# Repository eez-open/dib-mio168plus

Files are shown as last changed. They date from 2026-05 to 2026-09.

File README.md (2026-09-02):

### This is a WORK IN PROGRESS!

---

### Ownership and License
The contributors are listed in CONTRIB.TXT. 

Licenses | OSHWA UID
--|--
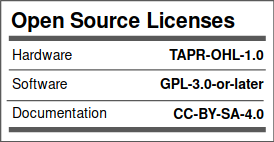
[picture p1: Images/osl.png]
osl
 | OSHW-HR000124 (https://certification.oshwa.org/hr000124.html)

### Overview

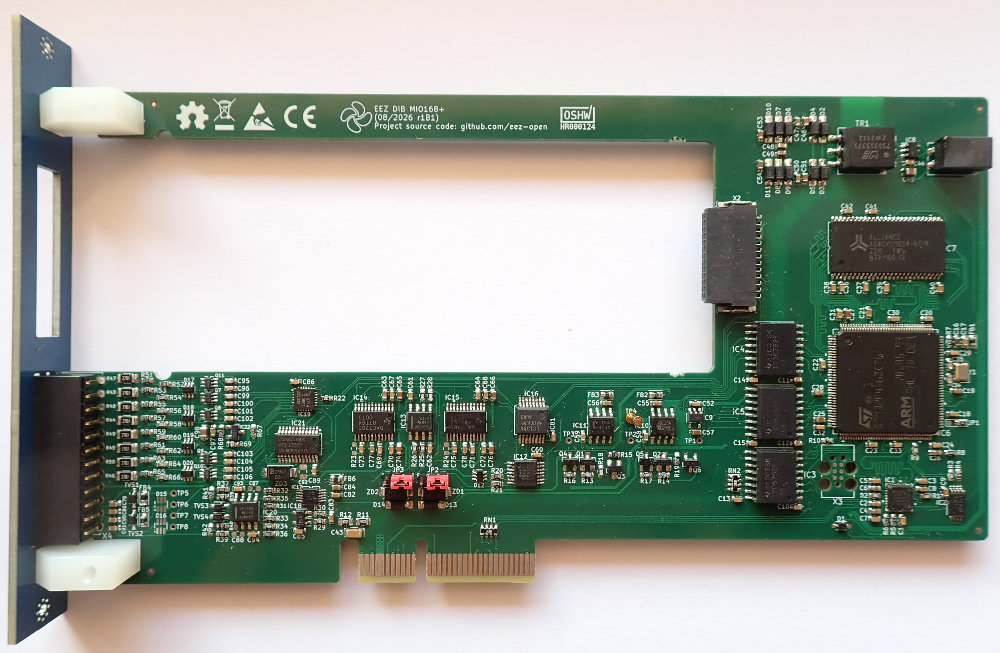
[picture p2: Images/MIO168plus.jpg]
MIO_empty


_Fig 1: MIO168+ without AFE module_

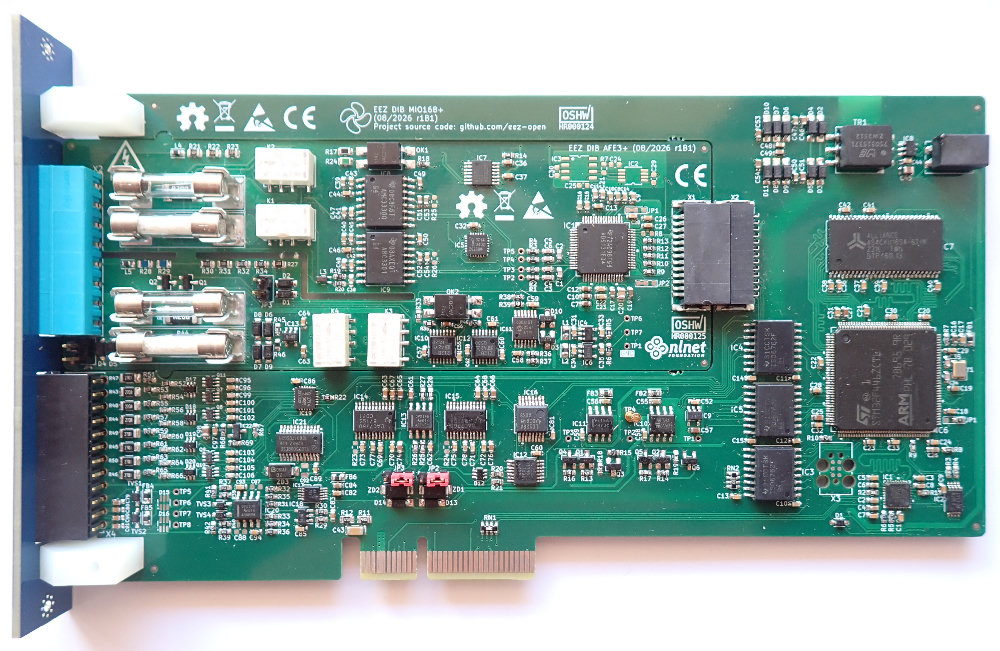
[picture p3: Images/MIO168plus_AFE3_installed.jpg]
MIO_AFE3


_Fig 2: MIO168+ with AFE3+ installed_

The MIO168+ module features multiple digital I/O, analog outputs and expansion connectors for carry various AFEs.

### Feature list

* On-board [STM32F446ZCT6](https://www.st.com/content/st_com/en/products/microcontrollers-microprocessors/stm32-32-bit-arm-cortex-mcus/stm32-high-performance-mcus/stm32f4-series/stm32f446/stm32f446zc.html) high-performance foundation line MCU, ARM Cortex-M4 with DSP and FPU, 256 KiB Flash, LQFP-144 package 
* AFE interface
* 8 x protected digital inputs (3.3/5/24 V), 2 x fast/slow, 6 x slow
* 8 x digital outputs with multiple protections, voltage clamp 24V, nom. current 330 mA (limit 2.3 A)
* 2 x PWM outputs (protected) or sensor bias power (+/-15 V, max. 10 mA)
* 2 x analog bipolar outputs (+/-5 V, +/-10 V, 0-5 V, 0-10 V). Voltage or current output with protection. 12-bit DAC, replaceable with pin compatible 14- or 16-bit version
* 2 x analog bipolar outputs +/-10 V. 12-bit DAC, replaceable with pin compatible 14- or 16-bit version
* On-board isolated power supply with +/-5.3 V outputs (with 4x multipliers), +/-15 V and +3.3 V LDO
* On-board SDRAM for measured data buffering (optional)
* USB HS PHY
* Firmware download via SPI or USB
* Optional SWD for debugging
* I2C EEPROM for storing board specific parameters
* Dimensions: 180 x 95 mm, 4-layer PCB

### Related topics and links

* [EEZ BB3+](https://github.com/eez-open/eez-bb3plus)
* [MIO168+ AFE3](https://github.com/eez-open/dib-mio168plus-afe3)
* [MIO168](https://github.com/eez-open/dib-mio168) for EEZ BB3 (retired)

---

This work is financed by [NLnet](https://nlnet.nl/project/BB3-CM5/) foundation

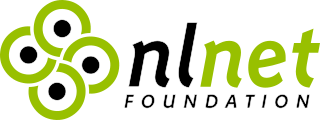
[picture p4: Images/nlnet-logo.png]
nlnet


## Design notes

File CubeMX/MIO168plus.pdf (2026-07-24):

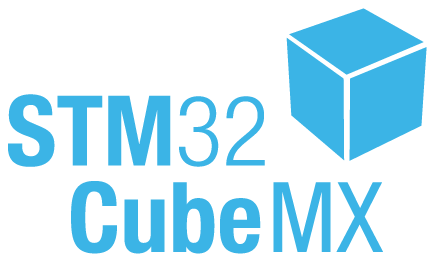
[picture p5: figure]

23/07/2026

MIO168plus Project
Configuration Report

## 1. Description

### 1.1. Project

Project Name | MIO168plus
Board Name | custom
Generated with: | STM32CubeMX 6.17.0
Date | 07/23/2026

### 1.2. MCU

MCU Series | STM32F4
MCU Line | STM32F446
MCU name | STM32F446ZETx
MCU Package | LQFP144
MCU Pin number | 144

### 1.3. Core(s) information

Core(s) | Arm Cortex-M4

## 2. Pinout Configuration

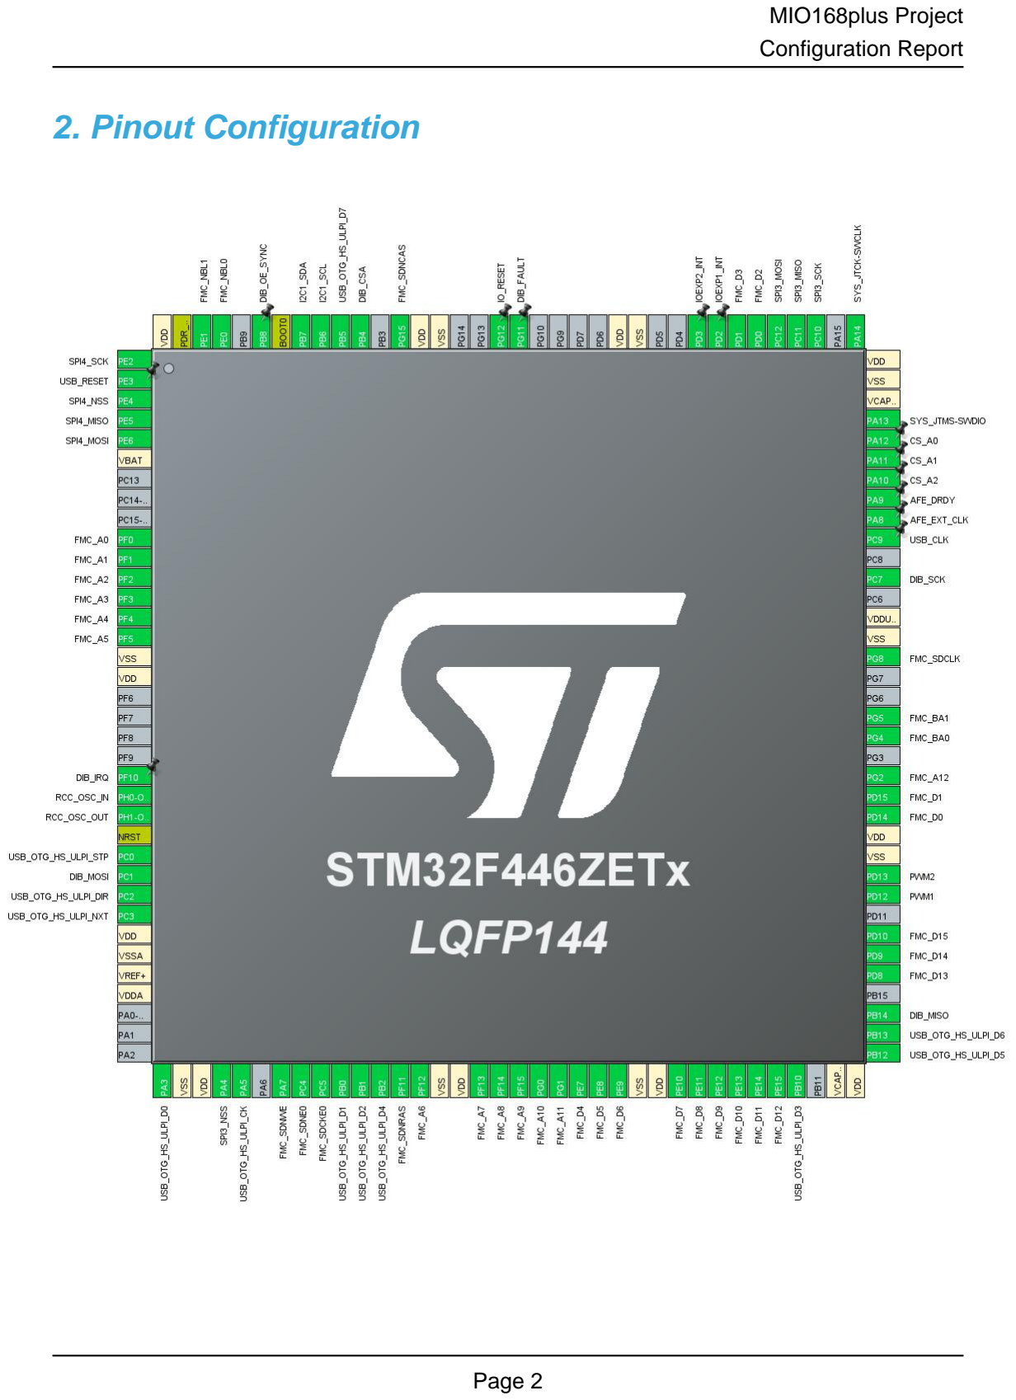
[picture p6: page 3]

## 3. Pins Configuration

Pin Number LQFP144 | Pin Name (function after reset) | Pin Type | Alternate Function(s) | Label
1 | PE2 | I/O | SPI4_SCK
2 | PE3 * | I/O | GPIO_Output | USB_RESET
3 | PE4 | I/O | SPI4_NSS
4 | PE5 | I/O | SPI4_MISO
5 | PE6 | I/O | SPI4_MOSI
6 | VBAT | Power
10 | PF0 | I/O | FMC_A0
11 | PF1 | I/O | FMC_A1
12 | PF2 | I/O | FMC_A2
13 | PF3 | I/O | FMC_A3
14 | PF4 | I/O | FMC_A4
15 | PF5 | I/O | FMC_A5
16 | VSS | Power
17 | VDD | Power
22 | PF10 * | I/O | GPIO_Output | DIB_IRQ
23 | PH0-OSC_IN | I/O | RCC_OSC_IN
24 | PH1-OSC_OUT | I/O | RCC_OSC_OUT
25 | NRST | Reset
26 | PC0 | I/O | USB_OTG_HS_ULPI_STP
27 | PC1 | I/O | SPI2_MOSI | DIB_MOSI
28 | PC2 | I/O | USB_OTG_HS_ULPI_DIR
29 | PC3 | I/O | USB_OTG_HS_ULPI_NXT
30 | VDD | Power
31 | VSSA | Power
32 | VREF+ | Power
33 | VDDA | Power
37 | PA3 | I/O | USB_OTG_HS_ULPI_D0
38 | VSS | Power
39 | VDD | Power
40 | PA4 | I/O | SPI3_NSS
41 | PA5 | I/O | USB_OTG_HS_ULPI_CK
43 | PA7 | I/O | FMC_SDNWE
44 | PC4 | I/O | FMC_SDNE0
45 | PC5 | I/O | FMC_SDCKE0
46 | PB0 | I/O | USB_OTG_HS_ULPI_D1
47 | PB1 | I/O | USB_OTG_HS_ULPI_D2

Pin Number LQFP144 | Pin Name (function after reset) | Pin Type | Alternate Function(s) | Label
48 | PB2 | I/O | USB_OTG_HS_ULPI_D4
49 | PF11 | I/O | FMC_SDNRAS
50 | PF12 | I/O | FMC_A6
51 | VSS | Power
52 | VDD | Power
53 | PF13 | I/O | FMC_A7
54 | PF14 | I/O | FMC_A8
55 | PF15 | I/O | FMC_A9
56 | PG0 | I/O | FMC_A10
57 | PG1 | I/O | FMC_A11
58 | PE7 | I/O | FMC_D4
59 | PE8 | I/O | FMC_D5
60 | PE9 | I/O | FMC_D6
61 | VSS | Power
62 | VDD | Power
63 | PE10 | I/O | FMC_D7
64 | PE11 | I/O | FMC_D8
65 | PE12 | I/O | FMC_D9
66 | PE13 | I/O | FMC_D10
67 | PE14 | I/O | FMC_D11
68 | PE15 | I/O | FMC_D12
69 | PB10 | I/O | USB_OTG_HS_ULPI_D3
71 | VCAP_1 | Power
72 | VDD | Power
73 | PB12 | I/O | USB_OTG_HS_ULPI_D5
74 | PB13 | I/O | USB_OTG_HS_ULPI_D6
75 | PB14 | I/O | SPI2_MISO | DIB_MISO
77 | PD8 | I/O | FMC_D13
78 | PD9 | I/O | FMC_D14
79 | PD10 | I/O | FMC_D15
81 | PD12 | I/O | TIM4_CH1 | PWM1
82 | PD13 | I/O | TIM4_CH2 | PWM2
83 | VSS | Power
84 | VDD | Power
85 | PD14 | I/O | FMC_D0
86 | PD15 | I/O | FMC_D1
87 | PG2 | I/O | FMC_A12
89 | PG4 | I/O | FMC_BA0
90 | PG5 | I/O | FMC_BA1

Pin Number LQFP144 | Pin Name (function after reset) | Pin Type | Alternate Function(s) | Label
93 | PG8 | I/O | FMC_SDCLK
94 | VSS | Power
95 | VDDUSB | Power
97 | PC7 | I/O | SPI2_SCK | DIB_SCK
99 | PC9 | I/O | RCC_MCO_2 | USB_CLK
100 | PA8 | I/O | RCC_MCO_1 | AFE_EXT_CLK
101 | PA9 | I/O | GPIO_EXTI9 | AFE_DRDY
102 | PA10 * | I/O | GPIO_Output | CS_A2
103 | PA11 * | I/O | GPIO_Output | CS_A1
104 | PA12 * | I/O | GPIO_Output | CS_A0
105 | PA13 | I/O | SYS_JTMS-SWDIO
106 | VCAP_2 | Power
107 | VSS | Power
108 | VDD | Power
109 | PA14 | I/O | SYS_JTCK-SWCLK
111 | PC10 | I/O | SPI3_SCK
112 | PC11 | I/O | SPI3_MISO
113 | PC12 | I/O | SPI3_MOSI
114 | PD0 | I/O | FMC_D2
115 | PD1 | I/O | FMC_D3
116 | PD2 | I/O | GPIO_EXTI2 | IOEXP1_INT
117 | PD3 | I/O | GPIO_EXTI3 | IOEXP2_INT
120 | VSS | Power
121 | VDD | Power
126 | PG11 | I/O | GPIO_EXTI11 | DIB_FAULT
127 | PG12 * | I/O | GPIO_Output | IO_RESET
130 | VSS | Power
131 | VDD | Power
132 | PG15 | I/O | FMC_SDNCAS
134 | PB4 | I/O | SPI2_NSS | DIB_CSA
135 | PB5 | I/O | USB_OTG_HS_ULPI_D7
136 | PB6 | I/O | I2C1_SCL
137 | PB7 | I/O | I2C1_SDA
138 | BOOT0 | Boot
139 | PB8 | I/O | GPIO_EXTI8 | DIB_OE_SYNC
141 | PE0 | I/O | FMC_NBL0
142 | PE1 | I/O | FMC_NBL1
143 | PDR_ON | Reset
144 | VDD | Power

* The pin is affected with an I/O function

## 4. Clock Tree Configuration

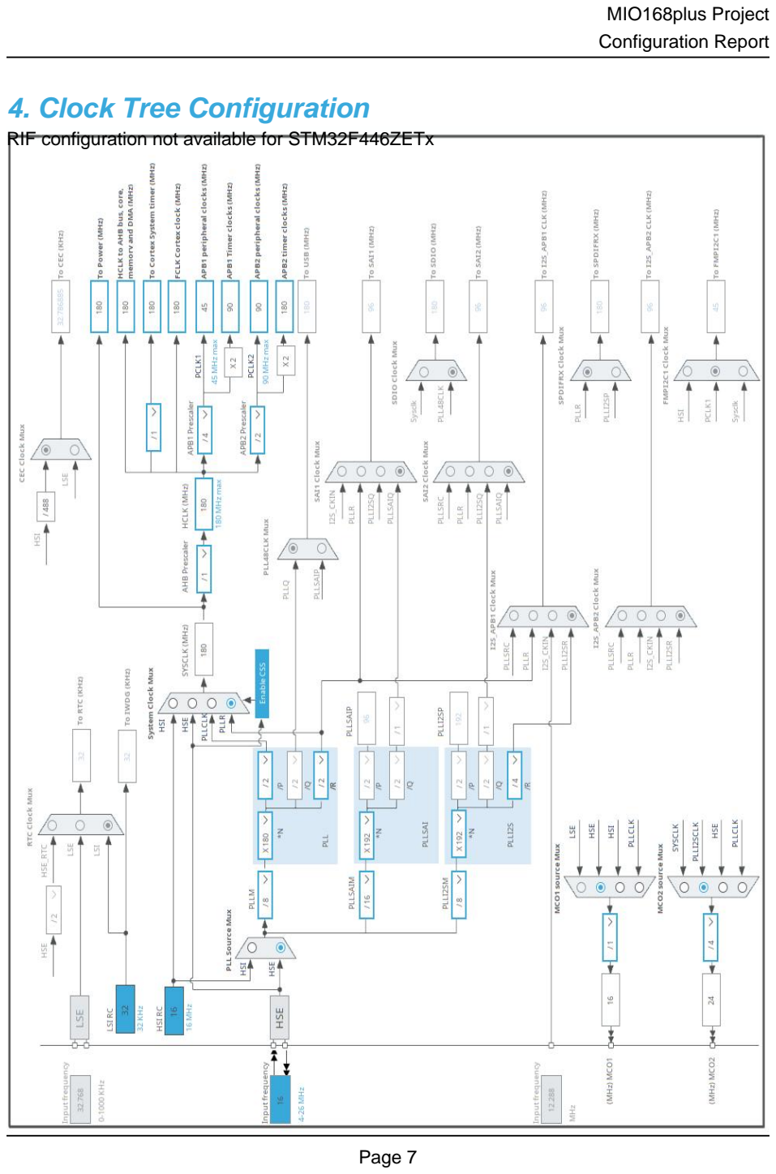
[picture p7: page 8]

RIF configuration not available for STM32F446ZETx

## 1. Power Consumption Calculator report

### 1.1. Microcontroller Selection

Series | STM32F4
Line | STM32F446
MCU | STM32F446ZETx
Datasheet | DS10693_Rev6

### 1.2. Parameter Selection

Temperature | 25
Vdd | 3.3

### 1.3. Battery Selection

Battery | Li-SOCL2(A3400)
Capacity | 3400.0 mAh
Self Discharge | 0.08 %/month
Nominal Voltage | 3.6 V
Max Cont Current | 100.0 mA
Max Pulse Current | 200.0 mA
Cells in series | 1
Cells in parallel | 1

### 1.4. Sequence

Step | Step1 | Step2
Mode | RUN | STOP_UDM (Under Drive)
Vdd | 3.3 | 3.3
Voltage Source | Battery | Battery
Range | Scale1-High | No Scale
Fetch Type | RAM/FLASH/REGON/ART/P REFETCH | n/a
CPU Frequency | 180 MHz | 0 Hz
Clock Configuration | HSE PLL | Regulator_LP Flash-PwrDwn
Clock Source Frequency | 4 MHz | 0 Hz
Peripherals
Additional Cons. | 0 mA | 0 mA
Average Current | 46 mA | 55 µA
Duration | 0.1 ms | 0.9 ms
DMIPS | 225.0 | 0.0
Ta Max | 99.99 | 104.99
Category | In DS Table | In DS Table

### 1.5. Results

Sequence Time | 1 ms | Average Current | 4.65 mA
Battery Life | 1 month | Average DMIPS | 225.0 DMIPS

### 1.6. Chart

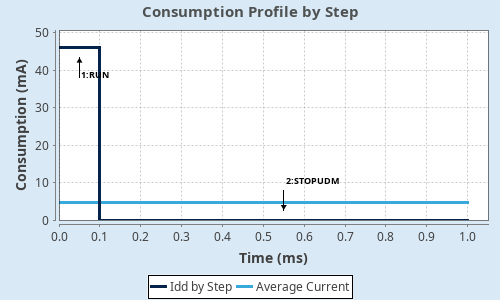
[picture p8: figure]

## 2. Software Project

### 2.1. Project Settings

Name | Value
Project Name | MIO168plus
Project Folder | /home/denis/git-public/dib-mio168plus/CubeMX
Toolchain / IDE | EWARM V8.50
Firmware Package Name and Version | STM32Cube FW_F4 V1.28.3
Application Structure | Advanced
Generate Under Root | No
Do not generate the main() | No
Minimum Heap Size | 0x200
Minimum Stack Size | 0x400

### 2.2. Code Generation Settings

Name | Value
STM32Cube MCU packages and embedded software | Copy all used libraries into the project folder
Generate peripheral initialization as a pair of '.c/.h' files | No
Backup previously generated files when re-generating | No
Keep User Code when re-generating | Yes
Delete previously generated files when not re-generated | Yes
Set all free pins as analog (to optimize the power consumption) | No
Enable Full Assert | No

### 2.3. Advanced Settings - Generated Function Calls

Rank | Function Name | Peripheral Instance Name
1 | SystemClock_Config | RCC
2 | MX_GPIO_Init | GPIO
3 | MX_FMC_Init | FMC
4 | MX_I2C1_Init | I2C1
5 | MX_SPI2_Init | SPI2
6 | MX_SPI3_Init | SPI3
7 | MX_SPI4_Init | SPI4
8 | MX_USB_OTG_HS_PCD_Init | USB_OTG_HS
9 | MX_TIM4_Init | TIM4

## 3. Peripherals and Middlewares Configuration

### 3.1. FMC

SDRAM 1
Clock and chip enable: SDCKE0+SDNE0
Internal bank number: 4 banks Address: 13 bits
Data: 16 bits
Byte enable: set
3.1.1. SDRAM 1:

SDRAM control:

Bank | SDRAM bank 1
Number of column address bits | 8 bits
Number of row address bits | 13 bits
CAS latency | 1 memory clock cycle
Write protection | Disabled
SDRAM common clock | Disabled
SDRAM common burst read | Disabled
SDRAM common read pipe delay | 0 HCLK clock cycle
SDRAM timing in memory clock cycles:
Load mode register to active delay | 16
Exit self-refresh delay | 16
Self-refresh time | 16
SDRAM common row cycle delay | 16
Write recovery time | 16
SDRAM common row precharge delay | 16
Row to column delay | 16

### 3.2. I2C1

I2C: I2C
3.2.1. Parameter Settings:

Master Features:

I2C Speed Mode | Standard Mode
I2C Clock Speed (Hz) | 100000
Slave Features:
Clock No Stretch Mode | Disabled

Primary Address Length selection | 7-bit
Dual Address Acknowledged | Disabled
Primary slave address | 0
General Call address detection | Disabled

### 3.3. RCC

High Speed Clock (HSE): Crystal/Ceramic Resonator mode: Master Clock Output 1
mode: Master Clock Output 2
3.3.1. Parameter Settings:

System Parameters:

VDD voltage (V) | 3.3
Instruction Cache | Enabled
Prefetch Buffer | Enabled
Data Cache | Enabled
Flash Latency(WS) | 5 WS (6 CPU cycle)
RCC Parameters:
HSI Calibration Value | 16
TIM Prescaler Selection | Disabled
HSE Startup Timout Value (ms) | 100
LSE Startup Timout Value (ms) | 5000
Power Parameters:
Power Regulator Voltage Scale | Power Regulator Voltage Scale 1
Power Over Drive | Enabled

### 3.4. SPI2

Mode: Full-Duplex Slave
Hardware NSS Signal: Hardware NSS Input Signal
3.4.1. Parameter Settings:

Basic Parameters:

Frame Format | Motorola
Data Size | 8 Bits
First Bit | MSB First
Clock Parameters:
Clock Polarity (CPOL) | Low

Clock Phase (CPHA) | 1 Edge
Advanced Parameters:
CRC Calculation | Disabled
NSS Signal Type | Input Hardware

### 3.5. SPI3

Mode: Full-Duplex Master
Hardware NSS Signal: Hardware NSS Output Signal
3.5.1. Parameter Settings:

Basic Parameters:

Frame Format | Motorola
Data Size | 8 Bits
First Bit | MSB First
Clock Parameters:
Prescaler (for Baud Rate) | 2
Baud Rate | 22.5 MBits/s *
Clock Polarity (CPOL) | Low
Clock Phase (CPHA) | 1 Edge
Advanced Parameters:
CRC Calculation | Disabled
NSS Signal Type | Output Hardware

### 3.6. SPI4

Mode: Full-Duplex Master
Hardware NSS Signal: Hardware NSS Output Signal
3.6.1. Parameter Settings:

Basic Parameters:

Frame Format | Motorola
Data Size | 8 Bits
First Bit | MSB First
Clock Parameters:
Prescaler (for Baud Rate) | 2
Baud Rate | 45.0 MBits/s *
Clock Polarity (CPOL) | Low
Clock Phase (CPHA) | 1 Edge

Advanced Parameters:

CRC Calculation | Disabled
NSS Signal Type | Output Hardware

### 3.7. SYS

Debug: Serial Wire
Timebase Source: SysTick

### 3.8. TIM4

Channel1: PWM Generation CH1 Channel2: PWM Generation CH2
3.8.1. Parameter Settings:

Counter Settings:

Prescaler (PSC - 16 bits value) | 0
Counter Mode | Up
Counter Period (AutoReload Register - 16 bits value ) | 65535
Internal Clock Division (CKD) | No Division
auto-reload preload | Disable
Trigger Output (TRGO) Parameters:
Master/Slave Mode (MSM bit) | Disable (Trigger input effect not delayed)
Trigger Event Selection | Reset (UG bit from TIMx_EGR)
PWM Generation Channel 1:
Mode | PWM mode 1
Pulse (16 bits value) | 0
Output compare preload | Enable
Fast Mode | Disable
CH Polarity | High
PWM Generation Channel 2:
Mode | PWM mode 1
Pulse (16 bits value) | 0
Output compare preload | Enable
Fast Mode | Disable
CH Polarity | High

### 3.9. USB_OTG_HS

External Phy: Device_Only
3.9.1. Parameter Settings:
Speed | Device High Speed 480MBit/s
Enable internal IP DMA | Disabled
Physical interface | External Phy
Low power | Disabled
Link Power Management | Disabled
Use dedicated end point 1 interrupt | Disabled
VBUS sensing | Disabled
Signal start of frame | Disabled

* User modified value

## 4. System Configuration

### 4.1. GPIO configuration

IP | Pin | Signal | GPIO mode | GPIO pull/up pull down

Max
Speed

User Label

FMC | PF0 | FMC_A0 | Alternate Function Push Pull | No pull-up and no pull-down | Very High
| PF1 | FMC_A1 | Alternate Function Push Pull | No pull-up and no pull-down | Very High
| PF2 | FMC_A2 | Alternate Function Push Pull | No pull-up and no pull-down | Very High
| PF3 | FMC_A3 | Alternate Function Push Pull | No pull-up and no pull-down | Very High
| PF4 | FMC_A4 | Alternate Function Push Pull | No pull-up and no pull-down | Very High
| PF5 | FMC_A5 | Alternate Function Push Pull | No pull-up and no pull-down | Very High
PA7 | FMC_SDNWE Alternate Function Push Pull | No pull-up and no pull-down | Very High
| PC4 | FMC_SDNE0 | Alternate Function Push Pull | No pull-up and no pull-down | Very High
PC5 | FMC_SDCKE0 Alternate Function Push Pull | No pull-up and no pull-down | Very High
PF11 | FMC_SDNRAS Alternate Function Push Pull | No pull-up and no pull-down | Very High
| PF12 | FMC_A6 | Alternate Function Push Pull | No pull-up and no pull-down | Very High
| PF13 | FMC_A7 | Alternate Function Push Pull | No pull-up and no pull-down | Very High
| PF14 | FMC_A8 | Alternate Function Push Pull | No pull-up and no pull-down | Very High
| PF15 | FMC_A9 | Alternate Function Push Pull | No pull-up and no pull-down | Very High
| PG0 | FMC_A10 | Alternate Function Push Pull | No pull-up and no pull-down | Very High
| PG1 | FMC_A11 | Alternate Function Push Pull | No pull-up and no pull-down | Very High
| PE7 | FMC_D4 | Alternate Function Push Pull | No pull-up and no pull-down | Very High
| PE8 | FMC_D5 | Alternate Function Push Pull | No pull-up and no pull-down | Very High
| PE9 | FMC_D6 | Alternate Function Push Pull | No pull-up and no pull-down | Very High
| PE10 | FMC_D7 | Alternate Function Push Pull | No pull-up and no pull-down | Very High
| PE11 | FMC_D8 | Alternate Function Push Pull | No pull-up and no pull-down | Very High
| PE12 | FMC_D9 | Alternate Function Push Pull | No pull-up and no pull-down | Very High
| PE13 | FMC_D10 | Alternate Function Push Pull | No pull-up and no pull-down | Very High
| PE14 | FMC_D11 | Alternate Function Push Pull | No pull-up and no pull-down | Very High
| PE15 | FMC_D12 | Alternate Function Push Pull | No pull-up and no pull-down | Very High
| PD8 | FMC_D13 | Alternate Function Push Pull | No pull-up and no pull-down | Very High
| PD9 | FMC_D14 | Alternate Function Push Pull | No pull-up and no pull-down | Very High
| PD10 | FMC_D15 | Alternate Function Push Pull | No pull-up and no pull-down | Very High
| PD14 | FMC_D0 | Alternate Function Push Pull | No pull-up and no pull-down | Very High
| PD15 | FMC_D1 | Alternate Function Push Pull | No pull-up and no pull-down | Very High
| PG2 | FMC_A12 | Alternate Function Push Pull | No pull-up and no pull-down | Very High
| PG4 | FMC_BA0 | Alternate Function Push Pull | No pull-up and no pull-down | Very High
| PG5 | FMC_BA1 | Alternate Function Push Pull | No pull-up and no pull-down | Very High
| PG8 | FMC_SDCLK | Alternate Function Push Pull | No pull-up and no pull-down | Very High
| PD0 | FMC_D2 | Alternate Function Push Pull | No pull-up and no pull-down | Very High
| PD1 | FMC_D3 | Alternate Function Push Pull | No pull-up and no pull-down | Very High

IP | Pin | Signal | GPIO mode | GPIO pull/up pull down

Max
Speed

User Label

PG15 | FMC_SDNCAS Alternate Function Push Pull | No pull-up and no pull-down | Very High
PE0 | FMC_NBL0 | Alternate Function Push Pull | No pull-up and no pull-down | Very High
PE1 | FMC_NBL1 | Alternate Function Push Pull | No pull-up and no pull-down | Very High
I2C1 | PB6 | I2C1_SCL | Alternate Function Open
Drain

No pull-up and no pull-down Very High
*
PB7 | I2C1_SDA | Alternate Function Open
Drain

No pull-up and no pull-down Very High
*
RCC | PH0-
OSC_IN
RCC_OSC_IN | n/a | n/a | n/a

PH1-
OSC_OUT
RCC_OSC_OUT | n/a | n/a | n/a
PC9 | RCC_MCO_2 | Alternate Function Push Pull | No pull-up and no pull-down | Low | USB_CLK
PA8 | RCC_MCO_1 | Alternate Function Push Pull | No pull-up and no pull-down | Low | AFE_EXT_CLK
SPI2 | PC1 | SPI2_MOSI | Alternate Function Push Pull | No pull-up and no pull-down | Very High
*

DIB_MOSI

PB14 | SPI2_MISO | Alternate Function Push Pull | No pull-up and no pull-down | Very High
*

DIB_MISO

PC7 | SPI2_SCK | Alternate Function Push Pull | No pull-up and no pull-down | Very High
*

DIB_SCK

PB4 | SPI2_NSS | Alternate Function Push Pull | No pull-up and no pull-down | Very High
*

DIB_CSA

SPI3 | PA4 | SPI3_NSS | Alternate Function Push Pull | No pull-up and no pull-down | Very High
*
PC10 | SPI3_SCK | Alternate Function Push Pull | No pull-up and no pull-down | Very High
*
PC11 | SPI3_MISO | Alternate Function Push Pull | No pull-up and no pull-down | Very High
*
PC12 | SPI3_MOSI | Alternate Function Push Pull | No pull-up and no pull-down | Very High
*
SPI4 | PE2 | SPI4_SCK | Alternate Function Push Pull | No pull-up and no pull-down | Very High
*
PE4 | SPI4_NSS | Alternate Function Push Pull | No pull-up and no pull-down | Very High
*
PE5 | SPI4_MISO | Alternate Function Push Pull | No pull-up and no pull-down | Very High
*
PE6 | SPI4_MOSI | Alternate Function Push Pull | No pull-up and no pull-down | Very High
*
SYS | PA13 | SYS_JTMS- | n/a | n/a | n/a

IP | Pin | Signal | GPIO mode | GPIO pull/up pull down

Max
Speed

User Label

SWDIO
| PA14 | SYS_JTCK- SWCLK | n/a | n/a | n/a
TIM4 | PD12 | TIM4_CH1 | Alternate Function Push Pull | No pull-up and no pull-down | Low | PWM1
| PD13 | TIM4_CH2 | Alternate Function Push Pull | No pull-up and no pull-down | Low | PWM2
USB_OTG_ HS | PC0 | USB_OTG_HS_ ULPI_STP | Alternate Function Push Pull | No pull-up and no pull-down | Very High
| PC2 | USB_OTG_HS_ ULPI_DIR | Alternate Function Push Pull | No pull-up and no pull-down | Very High
| PC3 | USB_OTG_HS_ ULPI_NXT | Alternate Function Push Pull | No pull-up and no pull-down | Very High
| PA3 | USB_OTG_HS_ ULPI_D0 | Alternate Function Push Pull | No pull-up and no pull-down | Very High
| PA5 | USB_OTG_HS_ ULPI_CK | Alternate Function Push Pull | No pull-up and no pull-down | Very High
| PB0 | USB_OTG_HS_ ULPI_D1 | Alternate Function Push Pull | No pull-up and no pull-down | Very High
| PB1 | USB_OTG_HS_ ULPI_D2 | Alternate Function Push Pull | No pull-up and no pull-down | Very High
| PB2 | USB_OTG_HS_ ULPI_D4 | Alternate Function Push Pull | No pull-up and no pull-down | Very High
| PB10 | USB_OTG_HS_ ULPI_D3 | Alternate Function Push Pull | No pull-up and no pull-down | Very High
| PB12 | USB_OTG_HS_ ULPI_D5 | Alternate Function Push Pull | No pull-up and no pull-down | Very High
| PB13 | USB_OTG_HS_ ULPI_D6 | Alternate Function Push Pull | No pull-up and no pull-down | Very High
| PB5 | USB_OTG_HS_ ULPI_D7 | Alternate Function Push Pull | No pull-up and no pull-down | Very High
GPIO | PE3 | GPIO_Output | Output Push Pull | No pull-up and no pull-down | Low | USB_RESET
| PF10 | GPIO_Output | Output Push Pull | No pull-up and no pull-down | Low | DIB_IRQ
| PA9 | GPIO_EXTI9 | External Interrupt Mode with Rising edge trigger detection | No pull-up and no pull-down | n/a | AFE_DRDY
| PA10 | GPIO_Output | Output Push Pull | No pull-up and no pull-down | Low | CS_A2
| PA11 | GPIO_Output | Output Push Pull | No pull-up and no pull-down | Low | CS_A1
| PA12 | GPIO_Output | Output Push Pull | No pull-up and no pull-down | Low | CS_A0
| PD2 | GPIO_EXTI2 | External Interrupt Mode with Rising edge trigger detection | No pull-up and no pull-down | n/a | IOEXP1_INT
| PD3 | GPIO_EXTI3 | External Interrupt Mode with Rising edge trigger detection | No pull-up and no pull-down | n/a | IOEXP2_INT
PG11 | GPIO_EXTI11 External Interrupt Mode with
| | | Rising edge trigger detection | No pull-up and no pull-down | n/a | DIB_FAULT
| PG12 | GPIO_Output | Output Push Pull | No pull-up and no pull-down | Low | IO_RESET
| PB8 | GPIO_EXTI8 | External Interrupt Mode with | No pull-up and no pull-down | n/a | DIB_OE_SYNC

IP | Pin | Signal | GPIO mode | GPIO pull/up pull down | Max Speed | User Label
| | | Rising edge trigger detection

### 4.2. DMA configuration

nothing configured in DMA service

### 4.3. NVIC configuration

4.3.1. NVIC
Interrupt Table | Enable | Preenmption Priority | SubPriority
Non maskable interrupt | true | 0 | 0
Hard fault interrupt | true | 0 | 0
Memory management fault | true | 0 | 0
Pre-fetch fault, memory access fault | true | 0 | 0
Undefined instruction or illegal state | true | 0 | 0
System service call via SWI instruction | true | 0 | 0
Debug monitor | true | 0 | 0
Pendable request for system service | true | 0 | 0
System tick timer | true | 15 | 0
PVD interrupt through EXTI line 16 | | unused
Flash global interrupt | | unused
RCC global interrupt | | unused
EXTI line 2 interrupt | | unused
EXTI line 3 interrupt | | unused
EXTI line[9:5] interrupts | | unused
TIM4 global interrupt | | unused
I2C1 event interrupt | | unused
I2C1 error interrupt | | unused
SPI2 global interrupt | | unused
EXTI line[15:10] interrupts | | unused
FMC global interrupt | | unused
SPI3 global interrupt | | unused
USB On The Go HS End Point 1 Out global interrupt | | unused
USB On The Go HS End Point 1 In global interrupt | | unused
USB On The Go HS global interrupt | | unused
FPU global interrupt | | unused
SPI4 global interrupt | | unused
4.3.2. NVIC Code generation

Enabled interrupt Table Select for init
sequence ordering
| | Generate IRQ
| | handler | Call HAL handler
Non maskable interrupt | false | true | false
Hard fault interrupt | false | true | false
Memory management fault | false | true | false
Pre-fetch fault, memory access fault | false | true | false

Enabled interrupt Table | Select for init sequence ordering | Generate IRQ handler | Call HAL handler
Undefined instruction or illegal state | false | true | false
System service call via SWI instruction | false | true | false
Debug monitor | false | true | false
Pendable request for system service | false | true | false
System tick timer | false | true | true

* User modified value

## 5. System Views

5.1. Category view
5.1.1. Current

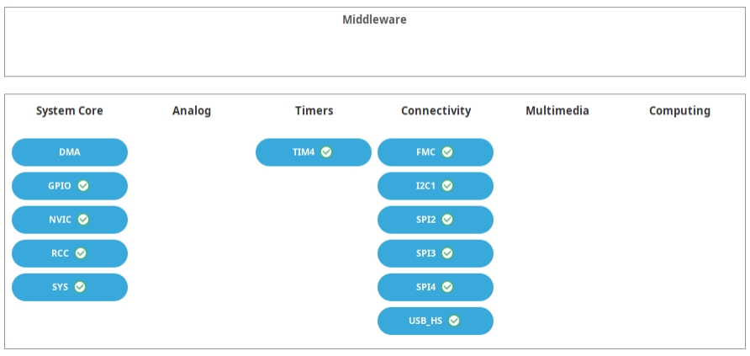
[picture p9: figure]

## 6. Docs & Resources

Type | Link
BSDL files | https://www.st.com/resource/en/bsdl_model/stm32f446_bsdl.zip
IBIS models | https://www.st.com/resource/en/ibis_model/stm32f446_ibis.zip
System View Description | https://www.st.com/resource/en/svd/stm32f4-svd.zip
Presentations | https://www.st.com/resource/en/product_presentation/stm32-stm8_embedded_software_solutions.pdf
Presentations | https://www.st.com/resource/en/product_presentation/stm32_eval-tools_portfolio.pdf
Presentations | https://www.st.com/resource/en/product_presentation/stm32_stm8_functi onal-safety-packages.pdf
Presentations | https://www.st.com/resource/en/product_presentation/stm32-stm8_software_development_tools.pdf
Presentations | https://www.st.com/resource/en/product_presentation/microcontrollers-stm32-family-overview.pdf
Brochures | https://www.st.com/resource/en/brochure/products-and-solutions-for-plcs-and-smart-i-os.pdf
Brochures | https://www.st.com/resource/en/brochure/expansion-boards-for-intelligent-power-switches.pdf
Flyers | https://www.st.com/resource/en/flyer/flstm32nucleo.pdf
Flyers | https://www.st.com/resource/en/flyer/flstm32trust.pdf
Product Certifications | https://www.st.com/resource/en/certification_document/stm32_authentication_can.pdf
Security Bulletin | https://www.st.com/resource/en/technical_note/tn1489-security-bulletin-tn1489stpsirt-physical-attacks-on-stm32-and-stm32cube-firmware-stmicroelectronics.pdf
Application Notes | https://www.st.com/resource/en/application_note/an1709-emc-design-guide-for-stm8-stm32-and-legacy-mcus-stmicroelectronics.pdf
Application Notes | https://www.st.com/resource/en/application_note/an2945-stm8s-and- stm32-mcus-a-consistent-832bit-product-line-for-painless-migration-

| stmicroelectronics.pdf
Application Notes | https://www.st.com/resource/en/application_note/an3070-managing-the-driver-enable-signal-for-rs485-and-iolink-communications-with-the-stm32s-usart-stmicroelectronics.pdf
Application Notes | https://www.st.com/resource/en/application_note/an3126-audio-and-waveform-generation-using-the-dac-in-stm32-products-stmicroelectronics.pdf
Application Notes | https://www.st.com/resource/en/application_note/an3155-usart-protocol-used-in-the-stm32-bootloader-stmicroelectronics.pdf
Application Notes | https://www.st.com/resource/en/application_note/an3156-usb-dfu-protocol-used-in-the-stm32-bootloader-stmicroelectronics.pdf
Application Notes | https://www.st.com/resource/en/application_note/an3364-migration-and-compatibility-guidelines-for-stm32-microcontroller-applications-stmicroelectronics.pdf
Application Notes | https://www.st.com/resource/en/application_note/an3997-audio-playback-and-recording-using-the-stm32f4discovery-stmicroelectronics.pdf
Application Notes | https://www.st.com/resource/en/application_note/an3998-pdm-audio-software-decoding-on-stm32-microcontrollers-stmicroelectronics.pdf
Application Notes | https://www.st.com/resource/en/application_note/an4031-using-the-stm32f2-stm32f4-and-stm32f7-series-dma-controller-stmicroelectronics.pdf
Application Notes | https://www.st.com/resource/en/application_note/an4221-i2c-protocol-used-in-the-stm32-bootloader-stmicroelectronics.pdf
Application Notes | https://www.st.com/resource/en/application_note/an4286-spi-protocol-used-in-the-stm32-bootloader-stmicroelectronics.pdf
Application Notes | https://www.st.com/resource/en/application_note/an4488-getting-started-with-stm32f4xxxx-mcu-hardware-development-stmicroelectronics.pdf
Application Notes | https://www.st.com/resource/en/application_note/an4640-peripherals-interconnections-on-stm32f4057xx-stm32f4157xx-stm32f42xxx-stm32f43xxx-stm32f446xx-and-stm32f469479xx-stmicroelectronics.pdf
Application Notes | https://www.st.com/resource/en/application_note/an4655-virtually-increasing-the-number-of-serial-communication-peripherals-in-stm32-applications-stmicroelectronics.pdf

Application Notes | https://www.st.com/resource/en/application_note/an4658-migration-of-applications-from-stm32f429439-lines-to-stm32f446-line-stmicroelectronics.pdf
Application Notes | https://www.st.com/resource/en/application_note/an4739-stm32cube-firmware-examples-for-stm32f4-series-stmicroelectronics.pdf
Application Notes | https://www.st.com/resource/en/application_note/an4750-handling-of-soft-errors-in-stm32-applications-stmicroelectronics.pdf
Application Notes | https://www.st.com/resource/en/application_note/an4776-generalpurpose-timer-cookbook-for-stm32-microcontrollers-stmicroelectronics.pdf
Application Notes | https://www.st.com/resource/en/application_note/an4803-highspeed-si-simulations-using-ibis-and-boardlevel-simulations-using-hyperlynx-si-on-stm32-mcus-and-mpus-stmicroelectronics.pdf
Application Notes | https://www.st.com/resource/en/application_note/an4850-stm32-mcus-spreadspectrum-clock-generation-principles-properties-and-implementation-stmicroelectronics.pdf
Application Notes | https://www.st.com/resource/en/application_note/an4989-stm32-microcontroller-debug-toolbox-stmicroelectronics.pdf
Application Notes | https://www.st.com/resource/en/application_note/an4995-using-an-electromyogram-technique-to-detect-muscle-activity-stmicroelectronics.pdf
Application Notes | https://www.st.com/resource/en/application_note/an5027-interfacing-pdm-digital-microphones-using-stm32-mcus-and-mpus-stmicroelectronics.pdf
Application Notes | https://www.st.com/resource/en/application_note/an5073-receiving-spdif-audio-stream-with-the-stm32f4f7h7-series-stmicroelectronics.pdf
Application Notes | https://www.st.com/resource/en/application_note/an4760-quadspi-interface-on-stm32-microcontrollers-and-microprocessors--stmicroelectronics.pdf
Application Notes | https://www.st.com/resource/en/application_note/an4899-stm32-microcontroller-gpio-hardware-settings-and-lowpower-consumption-stmicroelectronics.pdf
Application Notes | https://www.st.com/resource/en/application_note/an5612-esd-protection-of-stm32-mcus-and-mpus-stmicroelectronics.pdf
Application Notes | https://www.st.com/resource/en/application_note/an4838-introduction-to-

| memory-protection-unit-management-on-stm32-mcus-stmicroelectronics.pdf
Application Notes | https://www.st.com/resource/en/application_note/an4879-introduction-to-usb-hardware-and-pcb-guidelines-using-stm32-mcus-stmicroelectronics.pdf
Application Notes | https://www.st.com/resource/en/application_note/an5225-introduction-to-usb-typec-power-delivery-for-stm32-mcus-and-mpus-stmicroelectronics.pdf
Application Notes | https://www.st.com/resource/en/application_note/an5537-how-to-use-adc-oversampling-techniques-to-improve-signaltonoise-ratio-on-stm32-mcus-stmicroelectronics.pdf
Application Notes | https://www.st.com/resource/en/application_note/an5036-guidelines-for-thermal-management-on-stm32-applications-stmicroelectronics.pdf
Application Notes | https://www.st.com/resource/en/application_note/an4230-introduction-to-random-number-generation-validation-using-the-nist-statistical-test-suite-for-stm32-mcus-and-mpus-stmicroelectronics.pdf
Application Notes | https://www.st.com/resource/en/application_note/an2867-guidelines-for-oscillator-design-on-stm8afals-and-stm32-mcusmpus-stmicroelectronics.pdf
Application Notes | https://www.st.com/resource/en/application_note/an4013-introduction-to-timers-for-stm32-mcus-stmicroelectronics.pdf
Application Notes | https://www.st.com/resource/en/application_note/an4277-how-to-use-pwm-shutdown-for-motor-control-and-digital-power-conversion-on-stm32-mcus-stmicroelectronics.pdf
Application Notes | https://www.st.com/resource/en/application_note/an4759-introduction-to-using-the-hardware-realtime-clock-rtc-and-the-tamper-management-unit-tamp-with-stm32-mcus-stmicroelectronics.pdf
Application Notes | https://www.st.com/resource/en/application_note/an4908-getting-started-with-usart-automatic-baud-rater-detection-for-stm32-mcus-stmicroelectronics.pdf
Application Notes | https://www.st.com/resource/en/application_note/an5156-introduction-to-security-for-stm32-mcus-stmicroelectronics.pdf
Application Notes | https://www.st.com/resource/en/application_note/an5543-guidelines-for- enhanced-spi-communication-on-stm32-mcus-and-mpus-

| stmicroelectronics.pdf
Application Notes | https://www.st.com/resource/en/application_note/an5992-migrating-from-stm32f446-to-stm32h523533-mcus-stmicroelectronics.pdf
Application Notes | https://www.st.com/resource/en/application_note/cd00211314-how-to-optimize-the-adc-accuracy-in-the-stm32-mcus-stmicroelectronics.pdf
Application Notes | https://www.st.com/resource/en/application_note/an2639-soldering-recommendations-and-package-information-for-leadfree-ecopack2-mcus-and-mpus-stmicroelectronics.pdf
Application Notes | https://www.st.com/resource/en/application_note/an5020-introduction-to-digital-camera-interface-dcmi-for-stm32-mcus-stmicroelectronics.pdf
Application Notes | https://www.st.com/resource/en/application_note/an3154-how-to-use-can-protocol-in-bootloader-on-stm32-mcus-stmicroelectronics.pdf
Application Notes | https://www.st.com/resource/en/application_note/an4566-how-to-extend-the-dac-performance-on-stm32-mcus-stmicroelectronics.pdf
Application Notes | https://www.st.com/resource/en/application_note/an5647-the-goertzel-algorithm-to-compute-individual-terms-of-the-discrete-fourier-transform-dft-in-stm32-products-stmicroelectronics.pdf
Application Notes | https://www.st.com/resource/en/application_note/an2606-introduction-to-system-memory-boot-mode-on-stm32-mcus-stmicroelectronics.pdf
Application Notes for related Tools & Software | https://www.st.com/resource/en/application_note/an2656-stm32f10xxx-lcd-glass-driver-firmware-stmicroelectronics.pdf
Application Notes for related Tools & Software | https://www.st.com/resource/en/application_note/an2790-tft-lcd-interfacing-with-the-highdensity-stm32f10xxx-fsmc-stmicroelectronics.pdf
Application Notes for related Tools & Software | https://www.st.com/resource/en/application_note/an3078-stm32-inapplication-programming-over-the-ic-bus-stmicroelectronics.pdf
Application Notes for related Tools & Software | https://www.st.com/resource/en/application_note/an3116-stm32s-adc-modes-and-their-applications-stmicroelectronics.pdf

Application Notes
for related Tools

https://www.st.com/resource/en/application_note/an3174-implementingreceivers-for-infrared-remote-control-protocols-using-stm32f10xxx-

& Software | microcontrollers-stmicroelectronics.pdf
Application Notes for related Tools & Software | https://www.st.com/resource/en/application_note/an3241-qvga-tftlcd-direct-drive-using-the-stm32f10xx-fsmc-peripheral-stmicroelectronics.pdf
Application Notes for related Tools & Software | https://www.st.com/resource/en/application_note/an3307-guidelines-for-obtaining-iec-60335-class-b-certification-for-any-stm32-application-stmicroelectronics.pdf
Application Notes for related Tools & Software | https://www.st.com/resource/en/application_note/an3965-stm32f40xstm32f41x-inapplication-programming-using-the-usart-stmicroelectronics.pdf
Application Notes for related Tools & Software | https://www.st.com/resource/en/application_note/an3969-eeprom-emulation-in-stm32f40xstm32f41x-microcontrollers-stmicroelectronics.pdf
Application Notes for related Tools & Software | https://www.st.com/resource/en/application_note/an4044-floating-point-unit-demonstration-on-stm32-microcontrollers-stmicroelectronics.pdf
Application Notes for related Tools & Software | https://www.st.com/resource/en/application_note/an4323-getting-started-with-stemwin-library-stmicroelectronics.pdf
Application Notes for related Tools & Software | https://www.st.com/resource/en/application_note/an4365-using-stm32f4-mcu-power-modes-with-best-dynamic-efficiency-stmicroelectronics.pdf
Application Notes for related Tools & Software | https://www.st.com/resource/en/application_note/an4435-guidelines-for-obtaining-ulcsaiec-607301603351-class-b-certification-in-any-stm32-application-stmicroelectronics.pdf
Application Notes for related Tools & Software | https://www.st.com/resource/en/application_note/an4457-implementing-an-emulated-uart-on-stm32f4-microcontrollers-stmicroelectronics.pdf
Application Notes for related Tools & Software | https://www.st.com/resource/en/application_note/an4499-stm32--nrf51822-bluetooth-low-energy-system-solution-stmicroelectronics.pdf
Application Notes for related Tools & Software | https://www.st.com/resource/en/application_note/an4657-stm32-inapplication-programming-iap-using-the-usart-stmicroelectronics.pdf

Application Notes for related Tools & Software | https://www.st.com/resource/en/application_note/an4666-parallel-synchronous-transmission-using-gpio-and-dma-stmicroelectronics.pdf
Application Notes for related Tools & Software | https://www.st.com/resource/en/application_note/an4678-full-duplex-spi-emulation-for-stm32f4-microcontrollers-stmicroelectronics.pdf
Application Notes for related Tools & Software | https://www.st.com/resource/en/application_note/an4701-proprietary-code-readout-protection-on-microcontrollers-of-the-stm32f4-series-stmicroelectronics.pdf
Application Notes for related Tools & Software | https://www.st.com/resource/en/application_note/an4739-stm32cube-firmware-examples-for-stm32f4-series-stmicroelectronics.pdf
Application Notes for related Tools & Software | https://www.st.com/resource/en/application_note/an4758-proprietary-code-readout-protection-on-stm32l4-stm32l4-stm32g4-and-stm32wb-series-mcus-stmicroelectronics.pdf
Application Notes for related Tools & Software | https://www.st.com/resource/en/application_note/an4841-digital-signal-processing-for-stm32-microcontrollers-using-cmsis-stmicroelectronics.pdf
Application Notes for related Tools & Software | https://www.st.com/resource/en/application_note/an4852-programming-an-external-flash-memory-using-the-uart-bootloader-builtin-stm32-microcontrollers-stmicroelectronics.pdf
Application Notes for related Tools & Software | https://www.st.com/resource/en/application_note/an4968-proprietary-code-read-out-protection-pcrop-on-stm32f72xxx-and-stm32f73xxx-microcontrollers-stmicroelectronics.pdf
Application Notes for related Tools & Software | https://www.st.com/resource/en/application_note/an5056-integration-guide-for-the-xcubesbsfu-stm32cube-expansion-package-stmicroelectronics.pdf
Application Notes for related Tools & Software | https://www.st.com/resource/en/application_note/an5360-getting-started-with-projects-based-on-the-stm32mp1-series-in-stm32cubeide-stmicroelectronics.pdf
Application Notes for related Tools & Software | https://www.st.com/resource/en/application_note/an5361-getting-started-with-projects-based-on-dualcore-stm32h7-microcontrollers-in-stm32cubeide-stmicroelectronics.pdf
Application Notes | https://www.st.com/resource/en/application_note/an5394-getting-started-

for related Tools & Software | with-projects-based-on-the-stm32l5-series-in-stm32cubeide-stmicroelectronics.pdf
Application Notes for related Tools & Software | https://www.st.com/resource/en/application_note/an5418-how-to-build-a-simple-usbpd-sink-application-with-stm32cubemx-stmicroelectronics.pdf
Application Notes for related Tools & Software | https://www.st.com/resource/en/application_note/an5426-migrating-graphics-middleware-projects-from-stm32cubemx-540-to-stm32cubemx-550-stmicroelectronics.pdf
Application Notes for related Tools & Software | https://www.st.com/resource/en/application_note/an5464-position-control-of-a-threephase-permanent-magnet-motor-using-xcubemcsdk-or-xcubemcsdkful-stmicroelectronics.pdf
Application Notes for related Tools & Software | https://www.st.com/resource/en/application_note/an5564-getting-started-with-projects-based-on-dualcore-stm32wl-microcontrollers-in-stm32cubeide-stmicroelectronics.pdf
Application Notes for related Tools & Software | https://www.st.com/resource/en/application_note/an5698-adapting-the-xcubestl-functional-safety-package-for-stm32-iec-61508-compliant-to-other-safety-standards-stmicroelectronics.pdf
Application Notes for related Tools & Software | https://www.st.com/resource/en/application_note/an5731-stm32cubemx-and-stm32cubeide-threadsafe-solution-stmicroelectronics.pdf
Application Notes for related Tools & Software | https://www.st.com/resource/en/application_note/an4502-stm32-smbuspmbus-expansion-package-for-stm32cube-stmicroelectronics.pdf
Application Notes for related Tools & Software | https://www.st.com/resource/en/application_note/an5952-how-to-use-cmake-in-stm32cubeide-stmicroelectronics.pdf
Application Notes for related Tools & Software | https://www.st.com/resource/en/application_note/an5054-how-to-perform-secure-programming-using-stm32cubeprogrammer-stmicroelectronics.pdf
Application Notes for related Tools & Software | https://www.st.com/resource/en/application_note/an6179-how-to-integrate-the-stl-firmware-into-a-time-critical-user-application-stmicroelectronics.pdf

Application Notes
for related Tools

https://www.st.com/resource/en/application_note/an6127-getting-startedwith-stm32h7rx7sx-mcus-in-stm32cubeide-stmicroelectronics.pdf

& Software
Application Notes for related Tools & Software | https://www.st.com/resource/en/application_note/an6265-getting-started-with-stm32n6-mcus-in-stm32cubeide-stmicroelectronics.pdf
Application Notes for related Tools & Software | https://www.st.com/resource/en/application_note/an6382-introduction-to-swd-multidrop-for-stm32-with-stlink-stmicroelectronics.pdf
Errata Sheets | https://www.st.com/resource/en/errata_sheet/es0298-stm32f446xcxe-device-errata-stmicroelectronics.pdf
Datasheet | https://www.st.com/resource/en/datasheet/dm00141306.pdf
Programming Manuals | https://www.st.com/resource/en/programming_manual/pm0214-stm32-cortexm4-mcus-and-mpus-programming-manual-stmicroelectronics.pdf
Reference Manuals | https://www.st.com/resource/en/reference_manual/rm0390-stm32f446xx-advanced-armbased-32bit-mcus-stmicroelectronics.pdf
Technical Notes & Articles | https://www.st.com/resource/en/technical_note/tn0516-overview-of-the-stm32f0xf100xxf103xx-and-stm32f2xxf30xf4xx-mcus-pmsm-singledual-foc-sdk-v40-stmicroelectronics.pdf
Technical Notes & Articles | https://www.st.com/resource/en/technical_note/tn1163-description-of-wlcsp-for-microcontrollers-and-recommendations-for-its-use-stmicroelectronics.pdf
Technical Notes & Articles | https://www.st.com/resource/en/technical_note/tn1204-tape-and-reel-shipping-media-for-stm32-microcontrollers-in-bga-packages-stmicroelectronics.pdf
Technical Notes & Articles | https://www.st.com/resource/en/technical_note/tn1205-tape-and-reel-shipping-media-for-stm8-and-stm32-microcontrollers-in-fpn-packages-stmicroelectronics.pdf
Technical Notes & Articles | https://www.st.com/resource/en/technical_note/tn1206-tape-and-reel-shipping-media-for-stm8-and-stm32-microcontrollers-in-qfp-packages-stmicroelectronics.pdf
Technical Notes & Articles | https://www.st.com/resource/en/technical_note/tn1207-tape-and-reel-shipping-media-for-stm8-and-stm32-microcontrollers-in-so-packages-stmicroelectronics.pdf
Technical Notes | https://www.st.com/resource/en/technical_note/tn1208-tape-and-reel-

& Articles | shipping-media-for-stm8-and-stm32-microcontrollers-in-tssop-and-ssop-packages-stmicroelectronics.pdf
Technical Notes & Articles | https://www.st.com/resource/en/technical_note/tn1433-reference-device-marking-schematics-for-stm32-microcontrollers-and-microprocessors-stmicroelectronics.pdf
User Manuals | https://www.st.com/resource/en/user_manual/um3461-stm32f4-series-ulcsaiec-607301603351-selftest-library-user-guide-stmicroelectronics.pdf

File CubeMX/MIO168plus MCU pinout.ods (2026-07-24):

Pin Nb | PINs | FUNCTIONs | LABELs
1 | PE2 | SPI4_SCK
2 | PE3 | GPIO_Output | USB_RESET
3 | PE4 | SPI4_NSS
4 | PE5 | SPI4_MISO
5 | PE6 | SPI4_MOSI
10 | PF0 | FMC_A0
11 | PF1 | FMC_A1
12 | PF2 | FMC_A2
13 | PF3 | FMC_A3
14 | PF4 | FMC_A4
15 | PF5 | FMC_A5
22 | PF10 | GPIO_Output | DIB_IRQ
23 | PH0-OSC_IN | RCC_OSC_IN
24 | PH1-OSC_OUT | RCC_OSC_OUT
26 | PC0 | USB_OTG_HS_ULPI_STP
27 | PC1 | SPI2_MOSI | DIB_MOSI
28 | PC2 | USB_OTG_HS_ULPI_DIR
29 | PC3 | USB_OTG_HS_ULPI_NXT
37 | PA3 | USB_OTG_HS_ULPI_D0
40 | PA4 | SPI3_NSS
41 | PA5 | USB_OTG_HS_ULPI_CK
43 | PA7 | FMC_SDNWE
44 | PC4 | FMC_SDNE0
45 | PC5 | FMC_SDCKE0
46 | PB0 | USB_OTG_HS_ULPI_D1
47 | PB1 | USB_OTG_HS_ULPI_D2
48 | PB2 | USB_OTG_HS_ULPI_D4
49 | PF11 | FMC_SDNRAS
50 | PF12 | FMC_A6
53 | PF13 | FMC_A7
54 | PF14 | FMC_A8
55 | PF15 | FMC_A9
56 | PG0 | FMC_A10
57 | PG1 | FMC_A11
58 | PE7 | FMC_D4
59 | PE8 | FMC_D5
60 | PE9 | FMC_D6
63 | PE10 | FMC_D7
64 | PE11 | FMC_D8
65 | PE12 | FMC_D9
66 | PE13 | FMC_D10
67 | PE14 | FMC_D11
68 | PE15 | FMC_D12
69 | PB10 | USB_OTG_HS_ULPI_D3
73 | PB12 | USB_OTG_HS_ULPI_D5
74 | PB13 | USB_OTG_HS_ULPI_D6
75 | PB14 | SPI2_MISO | DIB_MISO
77 | PD8 | FMC_D13
78 | PD9 | FMC_D14
79 | PD10 | FMC_D15
81 | PD12 | TIM4_CH1 | PWM1
82 | PD13 | TIM4_CH2 | PWM2
85 | PD14 | FMC_D0
86 | PD15 | FMC_D1
87 | PG2 | FMC_A12
89 | PG4 | FMC_BA0
90 | PG5 | FMC_BA1
93 | PG8 | FMC_SDCLK
97 | PC7 | SPI2_SCK | DIB_SCK
99 | PC9 | RCC_MCO_2 | USB_CLK
100 | PA8 | RCC_MCO_1 | AFE_EXT_CLK
101 | PA9 | GPIO_EXTI9 | AFE_DRDY
102 | PA10 | GPIO_Output | CS_A2
103 | PA11 | GPIO_Output | CS_A1
104 | PA12 | GPIO_Output | CS_A0
105 | PA13 | SYS_JTMS-SWDIO
109 | PA14 | SYS_JTCK-SWCLK
111 | PC10 | SPI3_SCK
112 | PC11 | SPI3_MISO
113 | PC12 | SPI3_MOSI
114 | PD0 | FMC_D2
115 | PD1 | FMC_D3
116 | PD2 | GPIO_EXTI2 | IOEXP1_INT
117 | PD3 | GPIO_EXTI3 | IOEXP2_INT
126 | PG11 | GPIO_EXTI11 | DIB_FAULT
127 | PG12 | GPIO_Output | IO_RESET
132 | PG15 | FMC_SDNCAS
134 | PB4 | SPI2_NSS | DIB_CSA
135 | PB5 | USB_OTG_HS_ULPI_D7
136 | PB6 | I2C1_SCL
137 | PB7 | I2C1_SDA
139 | PB8 | GPIO_EXTI8 | DIB_OE_SYNC
141 | PE0 | FMC_NBL0
142 | PE1 | FMC_NBL1

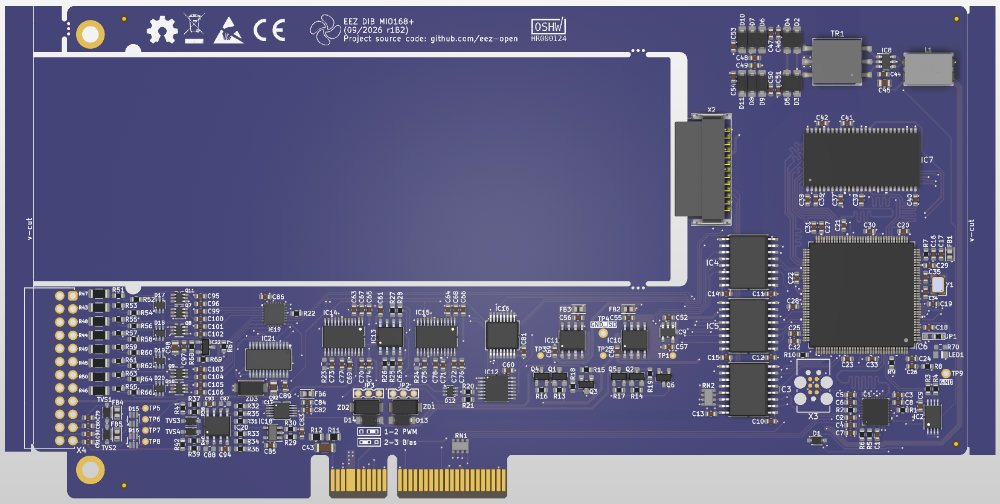
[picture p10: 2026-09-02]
Images/MIO168plus_3D.jpg

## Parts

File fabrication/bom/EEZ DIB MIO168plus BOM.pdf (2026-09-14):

EEZ DIB MIO168plus BOM, 14.09.2026

# | Reference | Value | Qty | DigiKey | Mouser | TME | LCSC

1 | | 100n | 57 | 490-4774-1-ND | 80-C0603C104M4R | CL10B104KA8NNNC | C14663
2 | 4u7/35V | 13 | 1276-6794-1-ND | GRM219R6YA475KA73D C913498
3 | C16,C47,C48,C49,C50,C55,C56 | 1u/50V | 7 | 1276-1860-1-ND | 187-CL10A105KB8NNNC CL10A105KB8NNNC | C15849
4 | C25,C27,C57 | 2u2 | 3 | 490-12738-1-ND | GRM188R61E225KA12D C77047
5 | C34,C35 | 10p | 2 | 1276-1069-1-ND | 187-CL10C100CB8NNNC VJ0603A100JXACW1BC C1634
6 | C43 | 4n7/1kV | 1 | 732-12074-2-ND | 710-885342208020 | 1206B472K102CT | C303960
7 | C45,C92,C98 | 10u | 3 | 490-5523-1-ND | GRM21BR61E106KA73L C15850
8 | C69,C71 | 2n2 | 2 | 490-4931-1-ND | GCM188R71H222KA37D C161225
9 | C77,C78 | 22n | 2 | 490-4933-1-ND | GCM188R71H223KA37D C161226
10 | C79,C80,C90,C91 | 1n | 4 | 1276-1018-2-ND | 187-CL10B102KB8NNNC CL10B102KB8NNNC | C1588
11 | C95,C99,C106 | 100p | 3 | 490-11153-1-ND | 81-GCM1885C1H101JA6J GCM1885C1H101JA16J C3868042
12 | C96,C100,C101,C102,C103,C104,C105 10n | 7 | 1276-1009-1-ND | 187-CL10B103KB8NNNC CL10B103KB8NNNC | C57112
13 | D1 | BAS316 | 1 | 1727-7370-1-ND | 771-BAS316-T/R | BAS316,115 | C109218
14 | MBR0530T3G | 12 | 863-MBR0530T3G | MBR0530T3GOSCT-ND MBR0530T3G | C236079
15 | D12,D17,D18,D19,D20 | BAT54XYH | 5 | 1727-2723-1-ND | 771-BAT54XYH | BAT54XY.115 | C549283
16 | FB1,FB2,FB3,FB4,FB5,FB6 | BLM18AG102SH1D | 6 | 490-7809-1-ND | 81-BLM18AG102SH1D | BLM18AG102SH1D | C337877
17 | IC1 | USB3300-EZK | 1 | 638-1034-ND | 886-USB3300-EZK | - | C108383
18 | IC2 | M24C32-DFDW6TP | 1 | 497-16067-1-ND | 511-M24C32-DFDW6TP M24C32-DFDW6TP | C2971426
19 | IC3,IC4,IC5 | ISO6762FDWR | 3 | 296-ISO6762FDWRCT-ND | 595-ISO6762FDWR | - | C5216396
20 | IC6 | STM32F446ZET6 | 1 | 497-15374-ND | 511-STM32F446ZET6 | STM32F446ZET6 | C1337227
21 | IC7 | IS42S16400N-6TL | 1 | 1450-1260-ND | 822-IM6416SDBATG-6I | - | C62379
22 | IC8 | SN6505BDBVT | 1 | 296-43154-2-ND | 595-SN6505BDBVT | - | C2156022
23 | IC9 | TPS7A2033PDBVR | 1 | 296-TPS7A2033PDBVRCT-ND | 595-TPS7A2033PDBVR | TPS7A2033PDBVR | C2862740
24 | IC10 | MC78L15ACDR2G | 1 | MC78L15ACDR2GOSDKR-ND | 863-MC78L15ACDR2G | L78L15ACD13TR | C233225
25 | IC11 | MC79L15ACDR2G | 1 | MC79L15ABDR2GOSDKR | 863-MC79L15ACDR2G | MC79L15ACDG | C148319
26 | IC12 | 74HC126PW,118 | 1 | 1727-6579-1-ND | 771-HC126PW118 | SN74HC126PWR | C507234
27 | IC13,IC20 | OPA2196IDR | 2 | 296-48159-1-ND | 595-OPA2196IDR | OPA2196IDR | C2057972
28 | IC14,IC15 | DAC7760IPWPR | 2 | 296-37188-1-ND | 595-DAC7760IPWPR | - | C2651670
29 | IC16 | SN74LVC138ADBR | 1 | 296-8460-1-ND | 595-SN74LVC138ADBR - | C2674435
30 | IC17 | DAC7563TDGSR | 1 | 296-43287-1-ND | 595-DAC7563TDGSR | - | C2879196
31 | IC18 | OPA376AIDBVR | 1 | 296-39130-2-ND | 595-OPA376AIDBVR | OPA376AIDBVR | C42134
32 | IC19 | PCAL9714HNMP | 1 | 568-PCAL9714HNMPCT-ND | 771-PCAL9714HNMP | - | C22444745
33 | IC21 | TLE75008ESDXUMA1 | 1 | 448-TLE75008ESDXUMA1CT-ND | | - | C2150432

C1,C2,C3,C5,C7,C9,C10,C11,C12,C13, C14,C15,C17,C18,C19,C20,C21,C22,C2 3,C24,C28,C29,C30,C31,C32,C33,C36, C37,C38,C39,C40,C41,C42,C44,C52,C5 8,C59,C60,C61,C62,C63,C64,C67,C68, C70,C72,C73,C75,C81,C82,C83,C85,C8 6,C89,C93,C94,C97
C4,C6,C8,C26,C46,C51,C53,C54,C65,C 66,C74,C76,C84

81-
GRM188R6YA475ME5D

81-
GRM188R61E225KA2D

81-
GRM21BR61E106KA3L
81-
GCM188R71H222K37D
81-
GCM188R71H223KA7J

D2,D3,D4,D5,D6,D7,D8,D9,D10,D11,D1 3,D14

726-
TLE75008ESDXUMA1

EEZ DIB MIO168plus BOM, 14.09.2026

34 | IC22 | TL431B | 1 | 296-17332-1-ND | 595-TL431IDBZR | L431QDBZR.215 | C21235
35 | JP2,JP3 | DS1025-01-1*3P8BV1-B | 2 | 952-1312-ND | 855-M22-2510305 | ZL303-03P | C3324237
36 | KK1,KK2 | PCB-MB-01 | 2 | RPC1760-ND | 144-PCB-MB-01 | RI-PCB-MB-01 | C959626
37 | L1 | SRF0905-202Y | 1 | SRF0905-202YCT-ND | 652-SRF0905-202Y | - | C2651160
38 | Q1 | MMBT5401 | 1 | MMBT5401-FDICT-ND | 621-MMBT5401-F | MMBT5401 | C21488
39 | Q2,Q3 | MMBT5551 | 2 | MMBT5551LT1GOSCT-ND | 863-MMBT5551LT1G | MMBT5551 | C83942
40 | Q4,Q6 | DMP3099L | 2 | DMP3099L-13DICT-ND | 621-DMP3099L-7 | DMP3099L-7 | C155244
41 | Q5 | 2N7002 | 1 | 2N7002LT1GOSCT-ND | 863-2N7002LT1G | 2N7002LT1G | C16338
42 | Q7,Q8,Q9,Q10,Q11 | NTJD5121NT1G | 5 | NTJD5121NT1GOSCT-ND | 863-NTJD5121NT1G | NTJD5121NT1G | C15215
43 | R1,R2,R25,R26,R27,R28 | 15R | 6 | 13-AC0603FR-0715RLCT-ND | 603-AC0603FR-0715RL | CQ0603-15R-1% | C144698
44 | R3,R4,R69 | 1K8 | 3 | 13-RC0603FR-131K8LCT-ND | 603-RC0603FR-131K8L | SMD0603-1K8-1% | C4177
45 | R5,R15,R68 | 470R | 3 | 13-AC0603FR-7W470RLCT-ND | 603-AC0603FR-7W470RL SMD0603-470R-1% | C20142029
46 | R6 | 12K | 1 | 13-RC0603FR-1312KLCT-ND | 603-RC0603FR-0712KL | SMD0603-12K-1% | C114659
47 | R7,R13,R14,R41,R42 | 47R | 5 | 13-RC0603FR-1347RLCT-ND | 603-RC0603FR-1347RL | SMD0603-47R-1% | C4328334
48 | R8 | 1R | 1 | 652-CR0603-F/1R00ELF SMD0603-1R-1% | C163871
49 | R9,R18,R19,R22 | 10K | 4 | 1712-CRGH0603F10KCT-ND | 756-WCR0603-10KFI | SMD0603-10K-1% | C25804
50 | R10 | 4K7 | 1 | 13-RC0603FR-134K7LTR-ND | 603-RC0603FR-134K7L | SMD0603-4K7-1% | C23162
51 | R11,R12 | 470K | 2 | A126370CT-ND | 71-CRCW0805470KFKEA 0805S8J0474T5E | C17709
52 | R16,R17 | 100K | 2 | 311-100KHRCT-ND | 603-RC0603FR-07100KL SMD0603-100K-1% | C25803
53 | R20,R21,R67 | 100R | 3 | 13-RC0603FR-10100RLCT-ND | 603-RC0603FR-10100RL RC0603FR-10100RL | C22775
54 | R29,R30,R31,R32,R33,R34 | 9K09 0.1% | 6 | YAG4788CT-ND | 603-RC0603BR-079K09L AR0603-9K09-0.1% | C185301
55 | R35,R36,R37,R39 | 75K 0.1% | 4 | YAG1730CT-ND | 603-RT0603BRD0775KL AR0603-75K-0.1% | C723587
56 | R38,R40 | 180R | 2 | 13-RC0603FR-13180RLCT-ND | 603-RC0603FR-13180RL SMD0603-180R-1% | C4077604
57 | R43,R44,R45,R46,R47,R48,R49,R50 | 2K7 | 8 | 311-2.70KFRCT-ND | 652-CR1206FX-2701ELF 1206S4F2701T5E | C205261
58 | R51,R53,R55,R57,R59,R61,R63,R65 | 27K | 8 | 311-27.0KHRCT-ND | 603-RC0603FR-0727KL | SMD0603-27K-1% | C114614
59 | R52,R54,R56,R58,R60,R62,R64,R66 | 1K | 8 | 13-RC0603FR-131KLCT-ND | 603-RC0603FR-131KL | CQ0603-1K-1% | C21190
60 | RN1,RN2 | CAY16-330J4LF | 2 | CAY16-330J4LFCT-ND | 652-CAY16-330J4LF | 4D03WGJ0330T | C840641
61 | TR1 | 750315371 | 1 | 1297-1178-1-ND | 710-750315371 | - | -
62 | TVS1,TVS2,TVS3,TVS4 | SD12C-7 | 4 | 31-SD12C-7CT-ND | 621-SD12C-7 | SD12C-7 | C1977377
63 | X2 | | 1 | | - | - | C5611301
64 | X4 | 1844824 | 1 | 1844824-ND | 651-1844824 | - | C6790362
65 | Y1 | | 1 | 535-14383-1-ND | | CX3225FB16000F0FZZ | C1986769
66 | ZD1,ZD2 | SMF16A | 2 | 4878-SMF16ATR-ND | 637-SMF16A | SMF16A-DIO | C207257
67 | ZD3 | SMF24A | 1 | 4878-SMF24ACT-ND | 637-SMF24A | SMF24A-DIO | C315999

118-CHP0603QFW-1R00ELFCT-ND

CBED202-
1379B001C1AD

4217-CBED202-
1379B001C1ADCT-ND

ABM8-16.000MHZ-10-
D7G-T

815-
ABM816.MHZ10D7GT

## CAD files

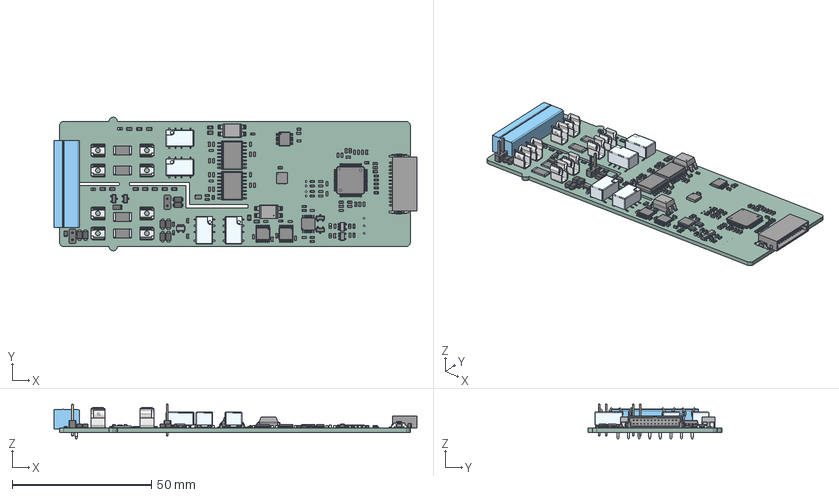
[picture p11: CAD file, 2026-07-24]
KiCad/MIO168plus AFE3.step
130.4 x 48.0 x 12.5 mm
C_0603_1608Metric x 60
R_0805_2012Metric x 15
R_0603_1608Metric x 23
ERJU1T0R00U x 4
IM03DGR x 4
BODY-SOIC x 2
LEAD-DW0016 x 32
PinsArrayL
PinsArrayR
PinHeader_1x02_P254mm_Vertical x 2
DG409LEDQ-T1-GE3 x 2
Body001 (Mirror #1) x 7
XY-plane x 12
X-axis x 12
GBED204-13-HSG
GBED204-Terminal2 x 13
GBED204-Terminal x 13
GBED204-Ground Piece x 2
R_1206_3216Metric
ThermalPin
PinsArrayLR
PinsArrayTB
MCP41HV51-103E_ST
BODY_VEC64A
LEAD_VEC64A x 64
CUI_DEVICES_TBP02R1-381-08BE
EEZ DIB AFE3plus_PCB

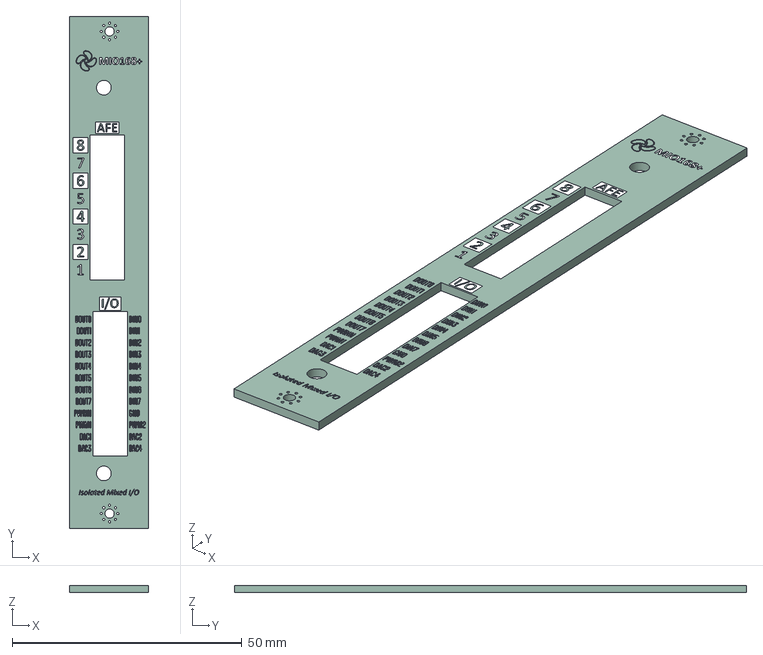
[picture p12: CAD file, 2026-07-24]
fabrication/step/MIO168plus front mask.step
17.2 x 111.5 x 1.58 mm
EEZ DIB MIO168plus front mask.kicad_pro_silkscreen
EEZ DIB MIO168plus front mask.kicad_pro_PCB

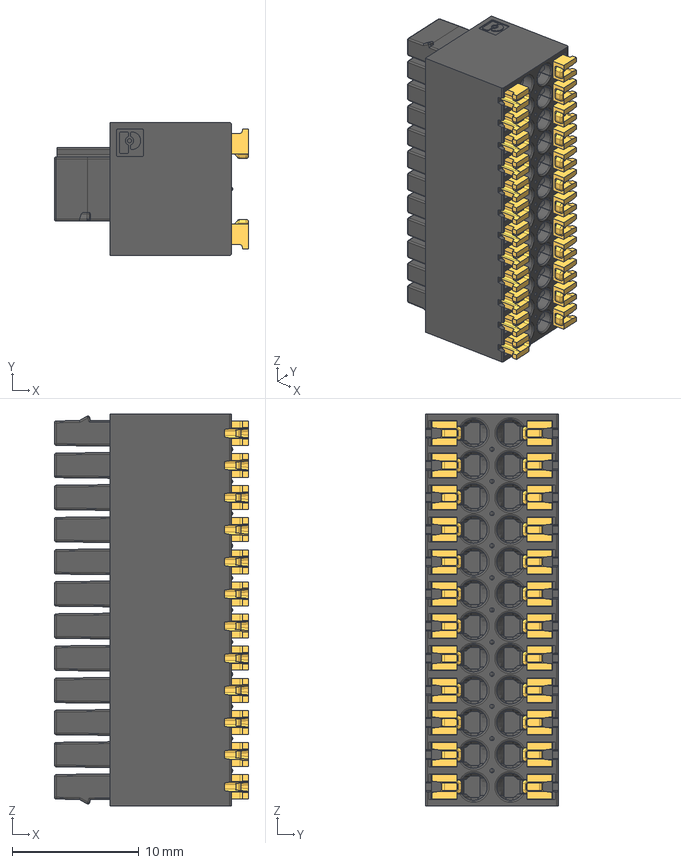
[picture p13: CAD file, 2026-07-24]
fabrication/step/1844675.stp
15.4 x 10.5 x 31.0 mm

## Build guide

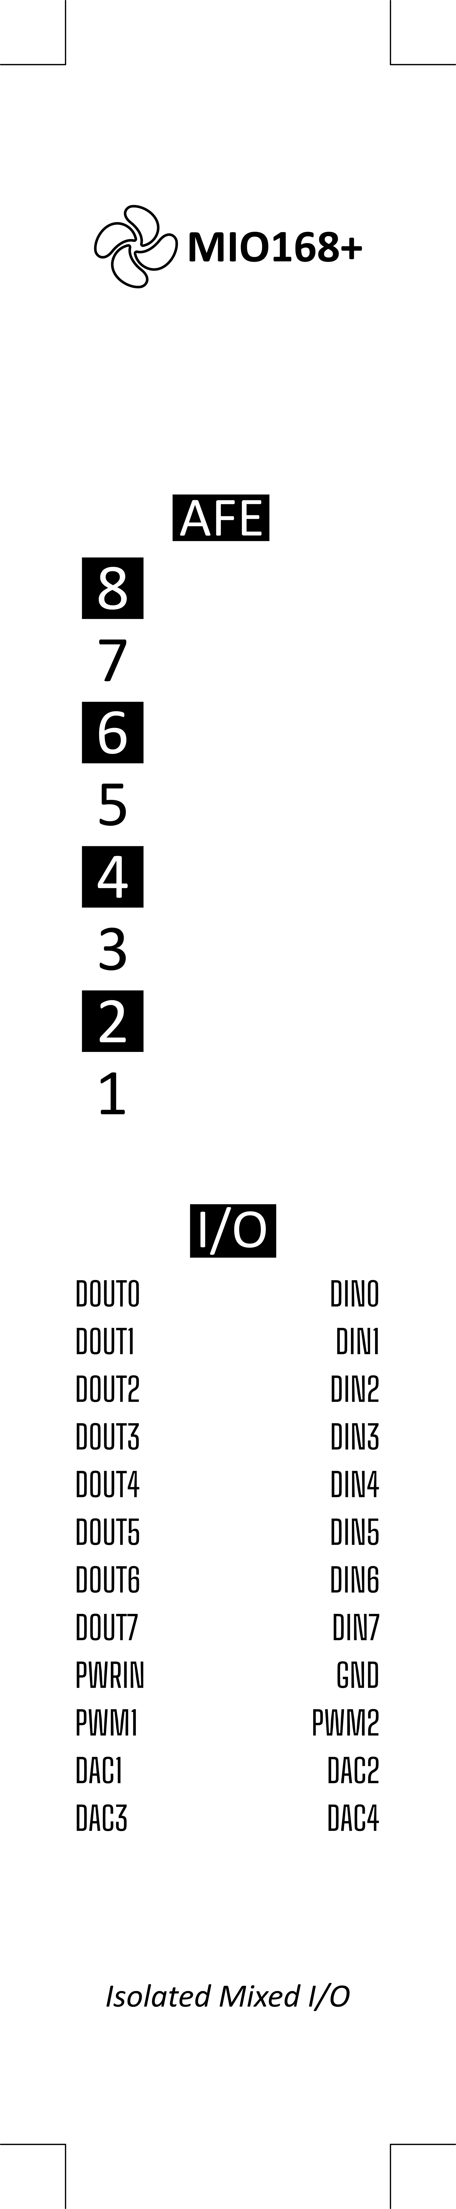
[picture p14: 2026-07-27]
fabrication/front mask/MIO168plus front mask.png

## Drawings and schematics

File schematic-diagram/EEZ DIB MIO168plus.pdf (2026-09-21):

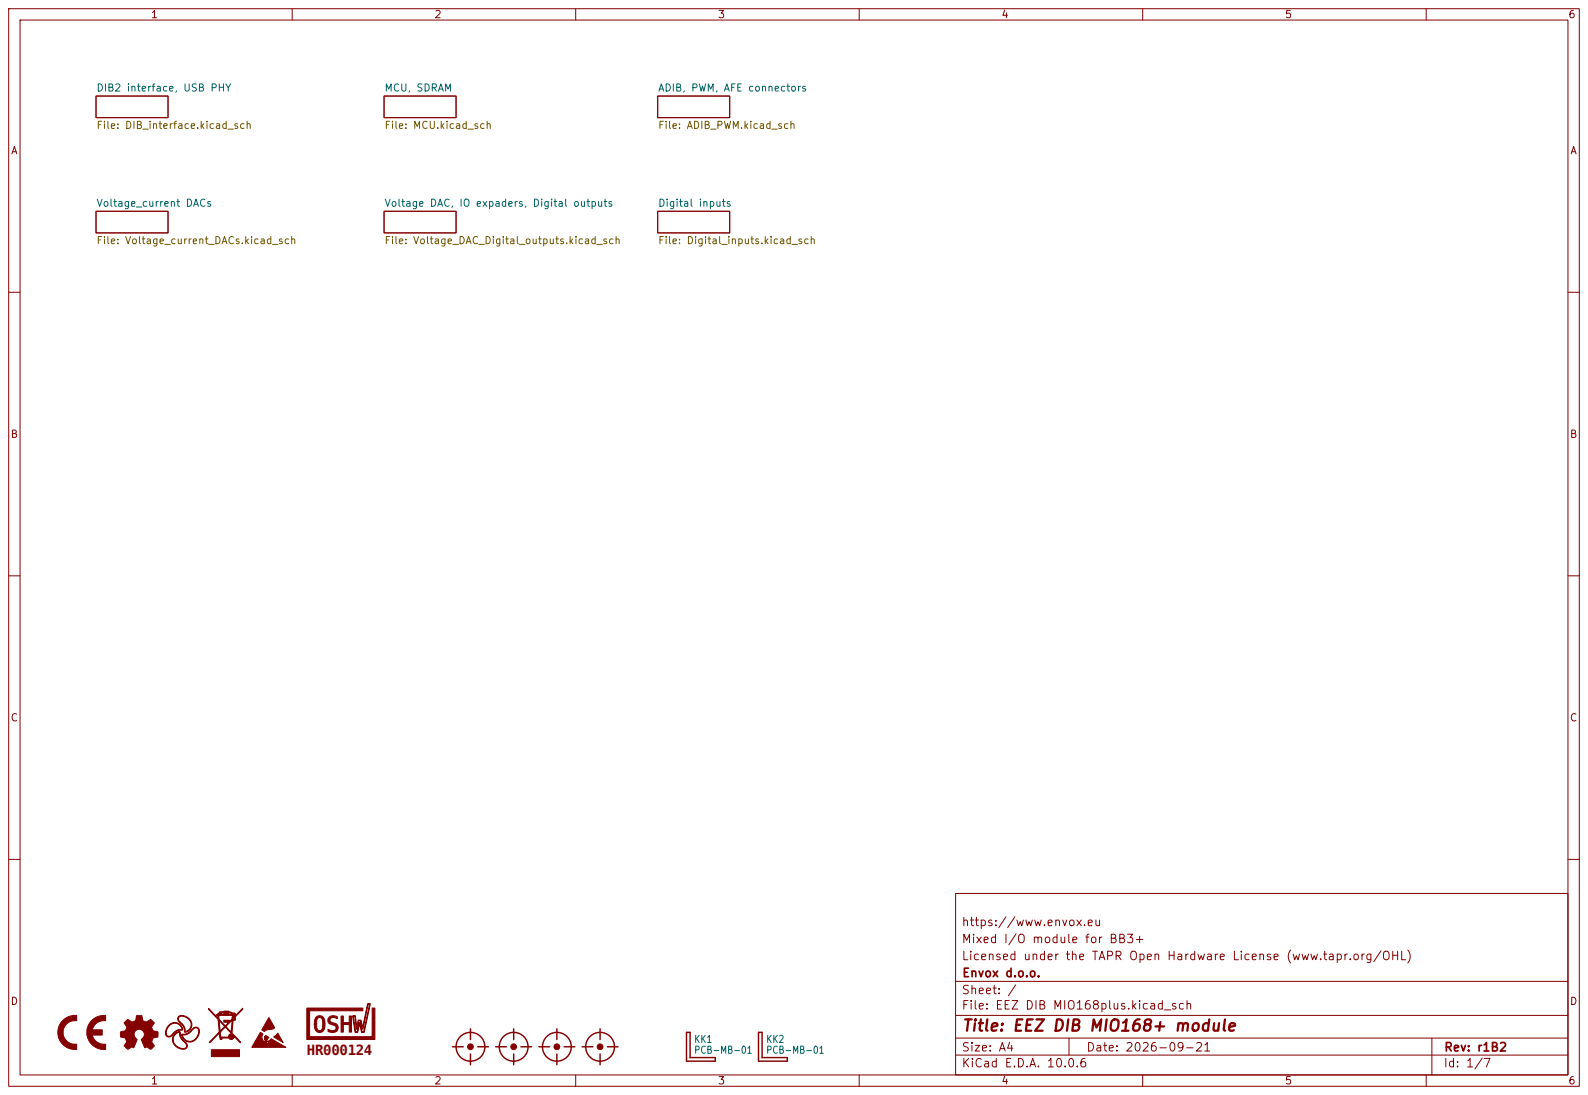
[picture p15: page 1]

File: MCU.kicad_sch DIB2 interface, USB PHY

ADIB, PWM, AFE connectors File: ADIB_PWM.kicad_sch

Voltage DAC, IO expaders, Digital outputs File: Voltage_DAC_Digital_outputs.kicad_sch

https://www.envox.eu
Mixed I/O module for BB3+
Licensed under the TAPR Open Hardware License (www.tapr.org/OHL)
Envox d.o.o.
Sheet: /
File: EEZ DIB MIO168plus.kicad_sch
Title: EEZ DIB MIO168+ module

Size: A4 | Rev: r1B2
KiCad E.D.A. 10.0.6 | Id: 1/7

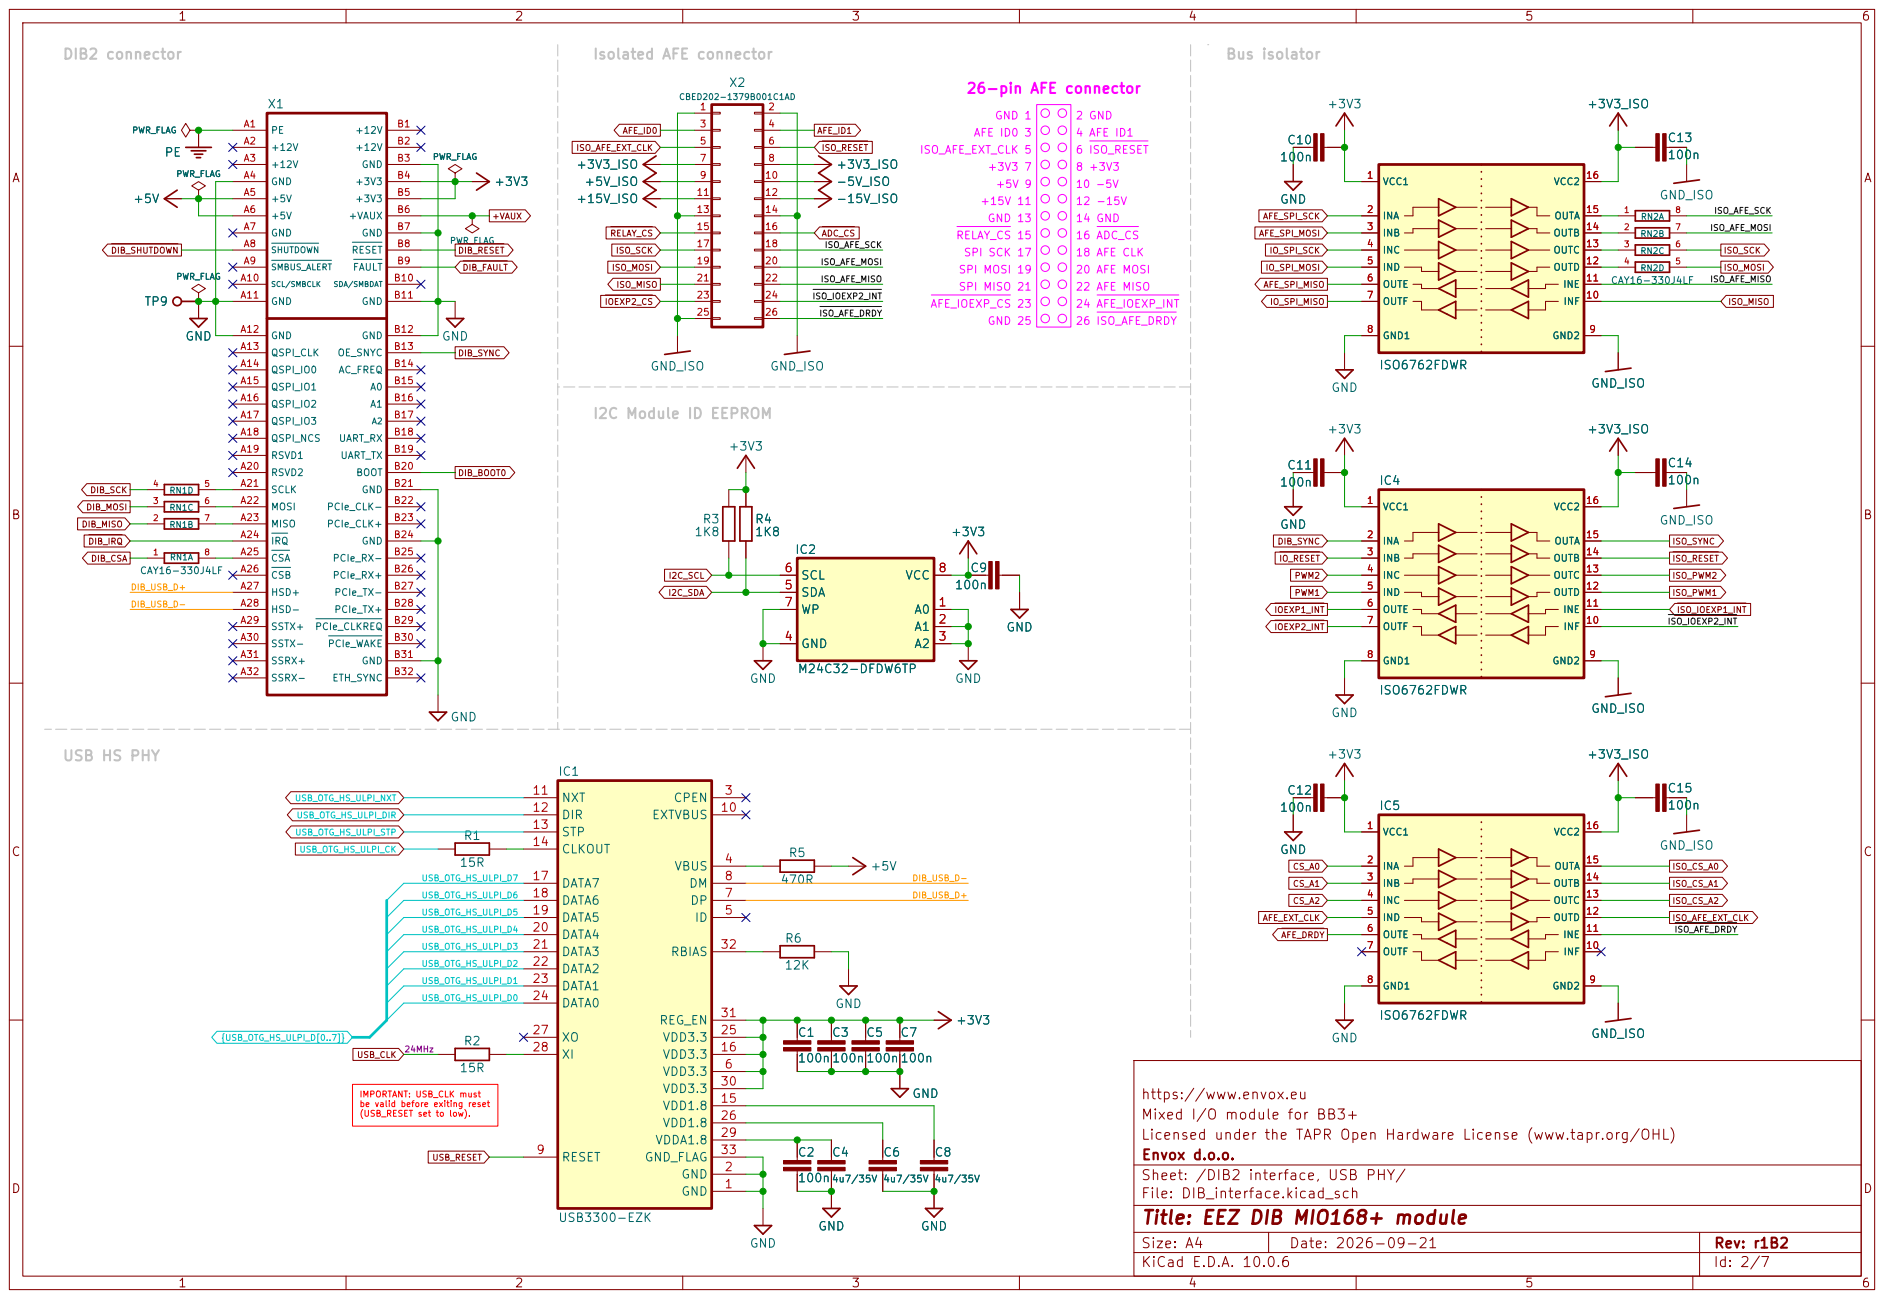
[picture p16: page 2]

6 ISO_RESET +3V3 7 GND 13 26-pin AFE connector AFE ID0 3 GND 1
GND -5V_ISO

IMPORTANT: USB_CLK must be valid before exiting reset (USB_RESET set to low).

https://www.envox.eu
Mixed I/O module for BB3+
Licensed under the TAPR Open Hardware License (www.tapr.org/OHL)
Envox d.o.o.
Sheet: /DIB2 interface, USB PHY/
File: DIB_interface.kicad_sch
Title: EEZ DIB MIO168+ module

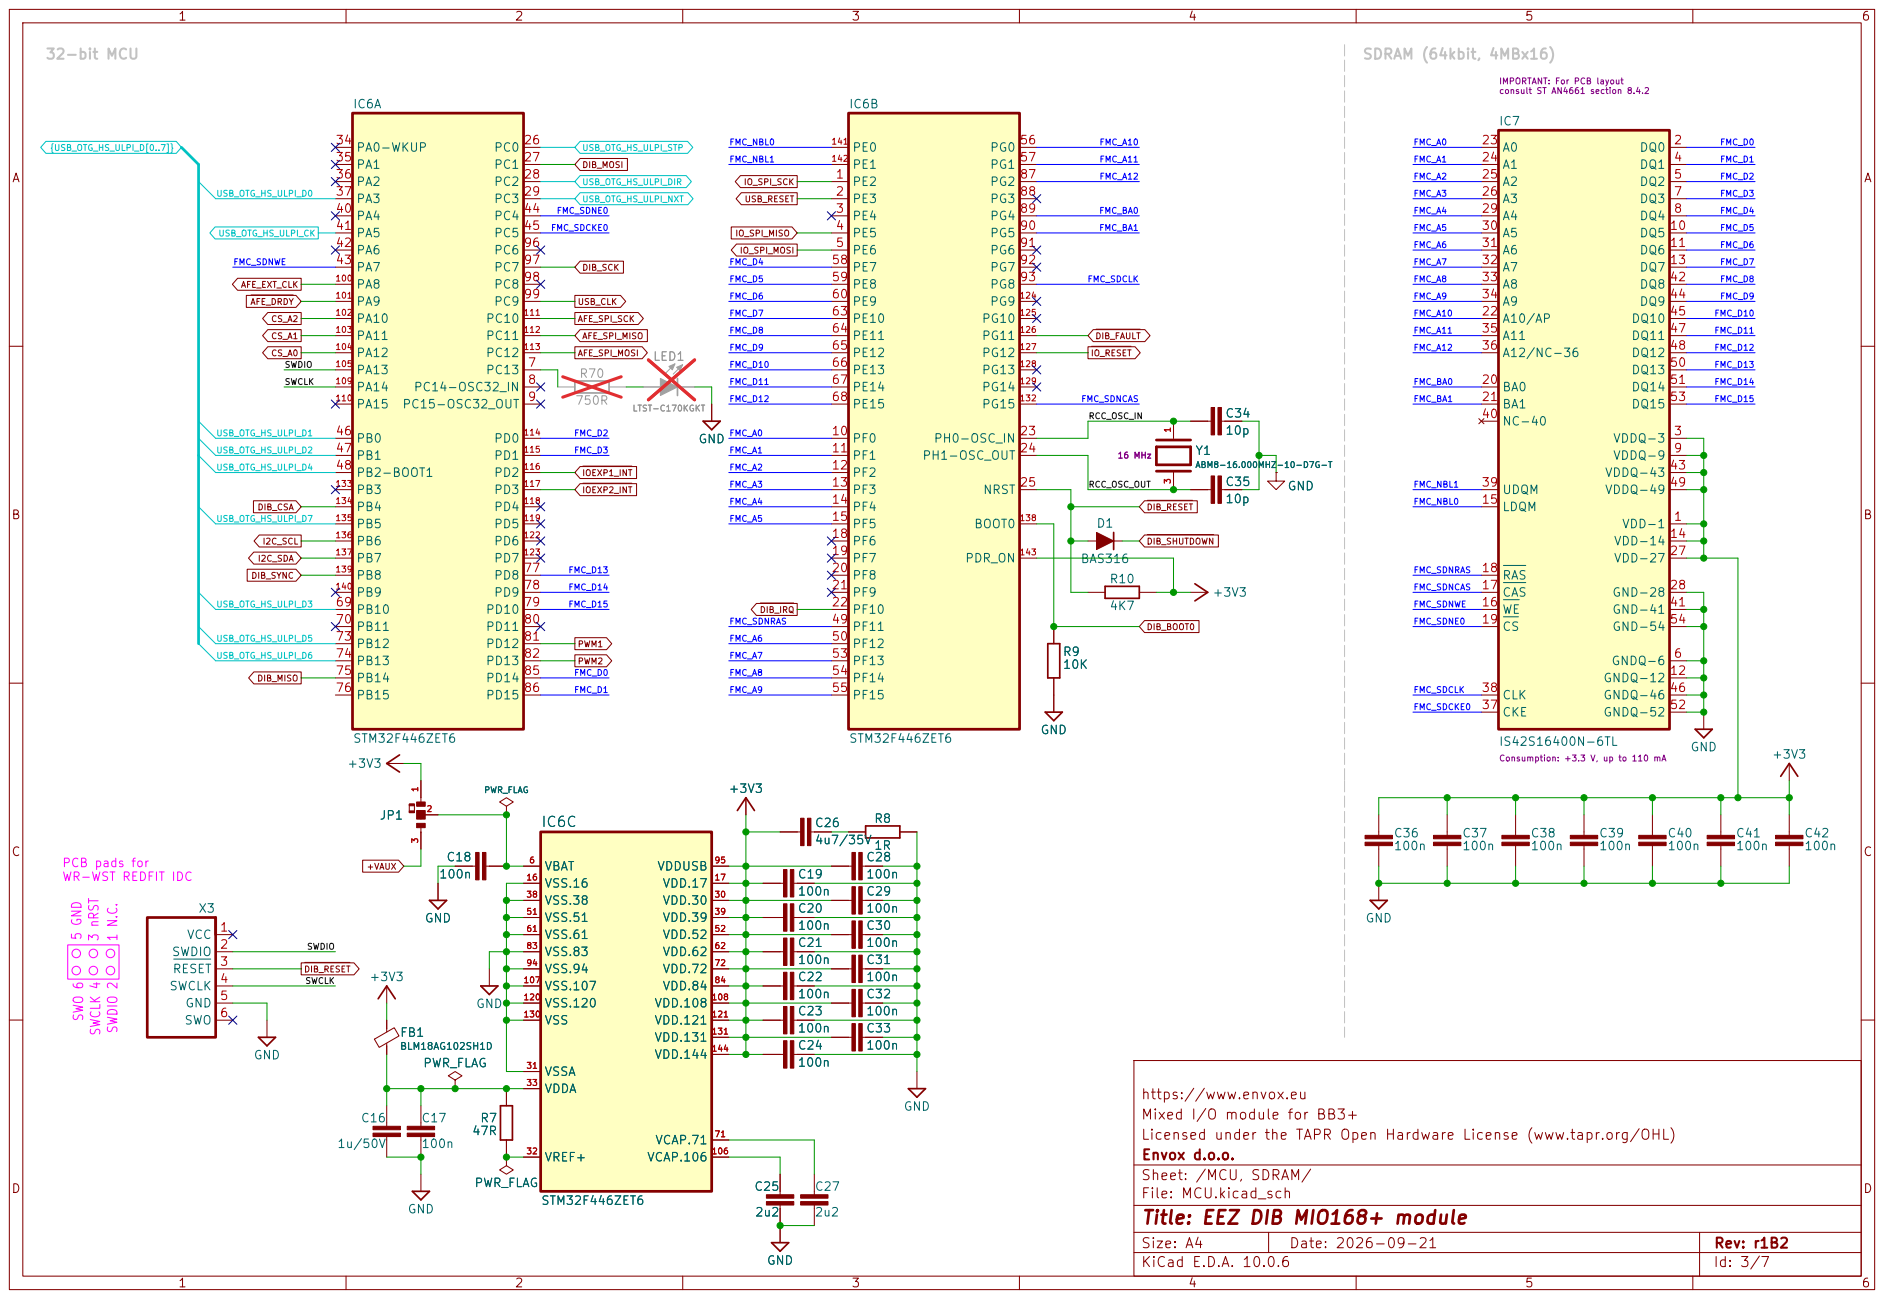
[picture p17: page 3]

Consumption: +3.3 V, up to 110 mA LED1

https://www.envox.eu
Mixed I/O module for BB3+
Licensed under the TAPR Open Hardware License (www.tapr.org/OHL)
Envox d.o.o.
Sheet: /MCU, SDRAM/
File: MCU.kicad_sch
Title: EEZ DIB MIO168+ module

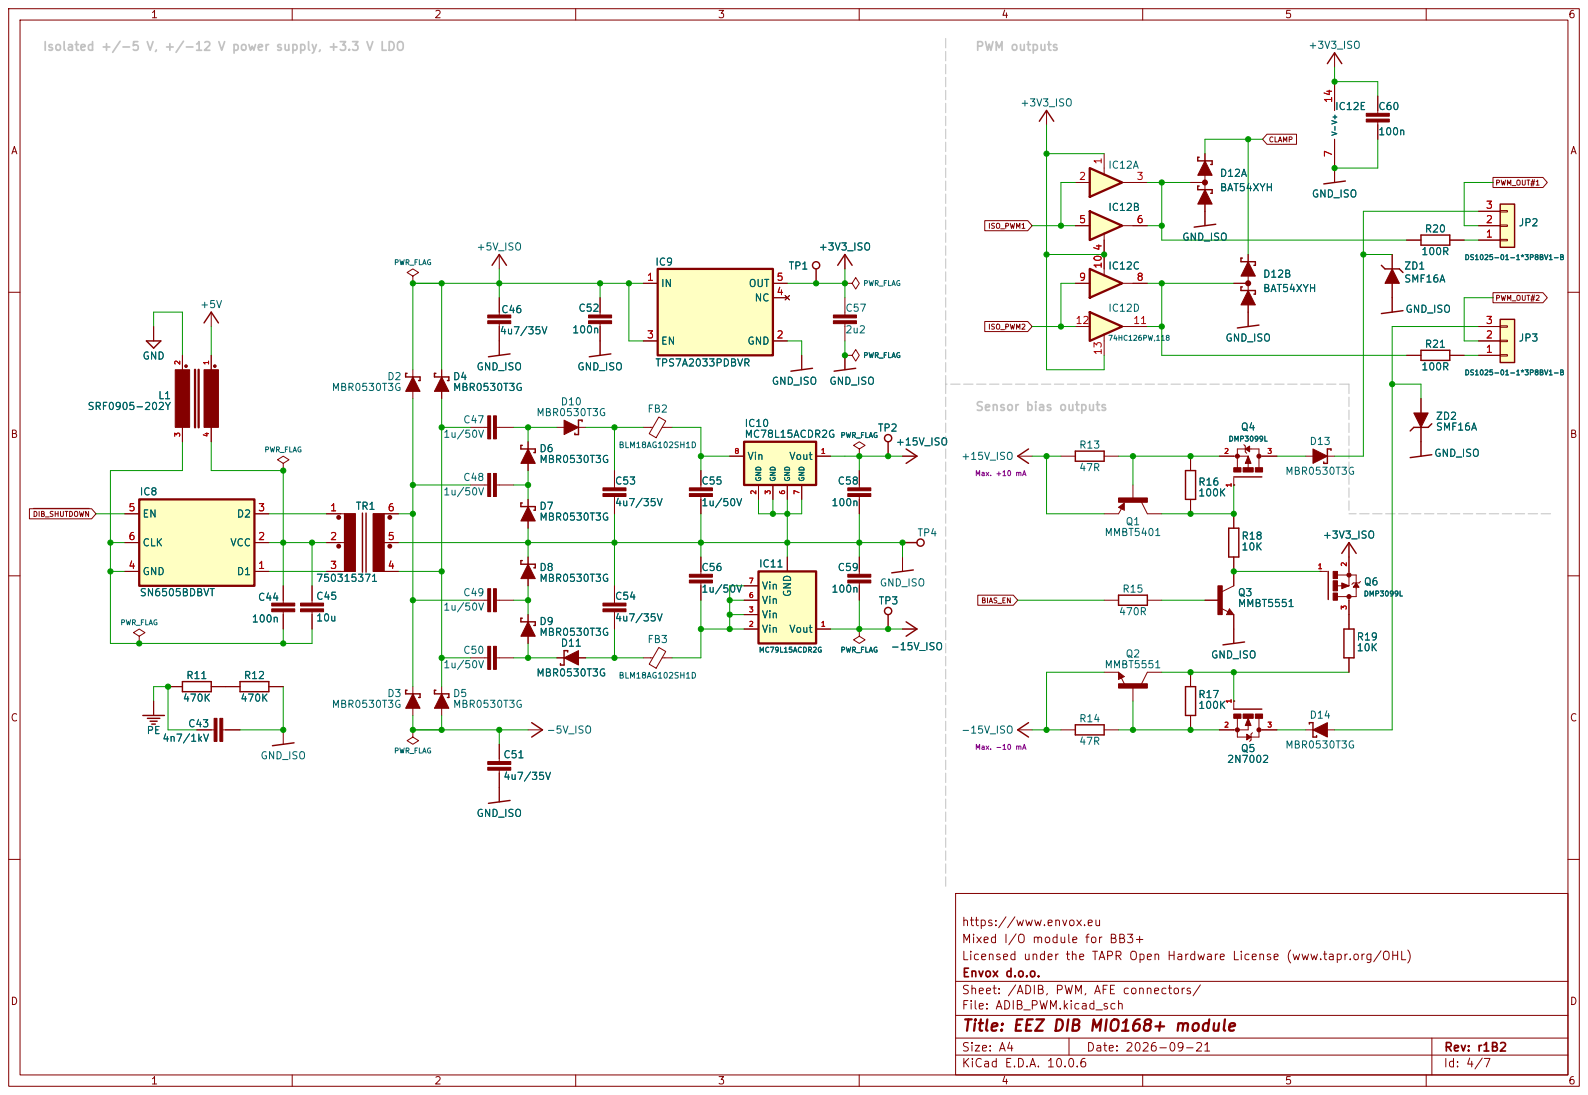
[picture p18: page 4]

Isolated +/-5 V, +/-12 V power supply, +3.3 V LDO

Max. -10 mA Max. +10 mA PWM outputs GND

https://www.envox.eu
Mixed I/O module for BB3+
Licensed under the TAPR Open Hardware License (www.tapr.org/OHL)
Envox d.o.o.
Sheet: /ADIB, PWM, AFE connectors/
File: ADIB_PWM.kicad_sch
Title: EEZ DIB MIO168+ module

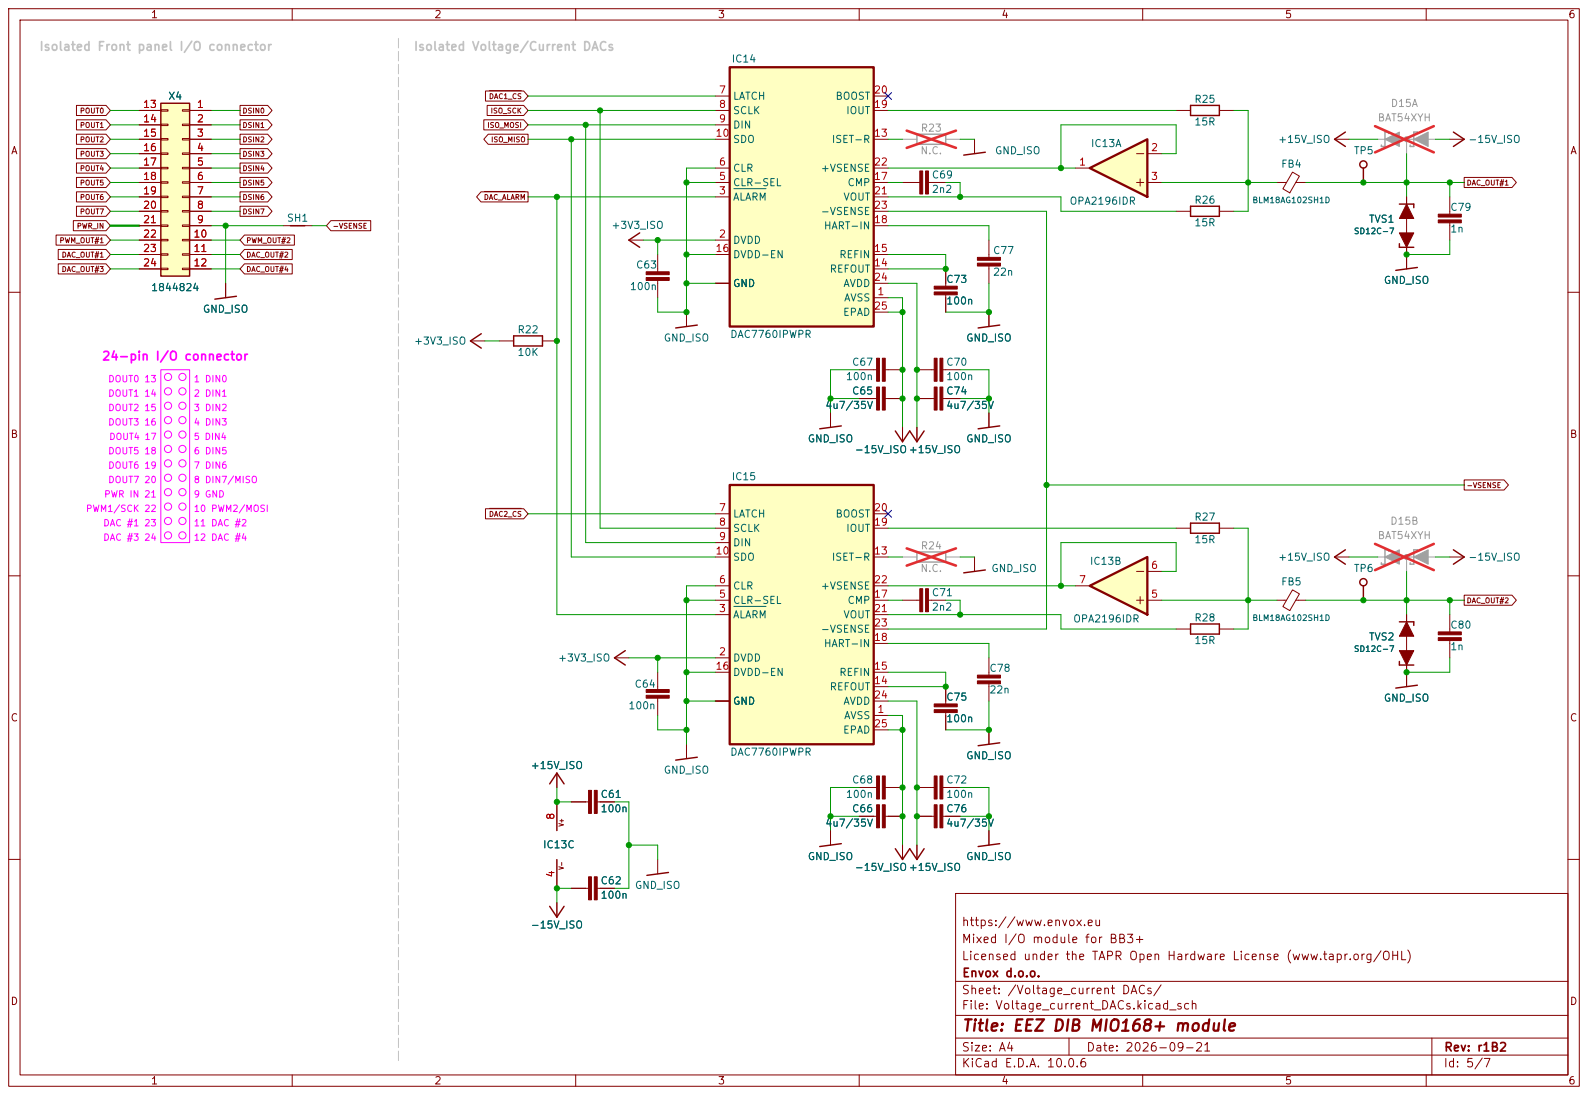
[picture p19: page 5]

11 DAC #2 DOUT5 18 DOUT6 19 DOUT4 17 24-pin I/O connector DOUT2 15 PWM1/SCK 22 DAC #1 23 DAC #3 24 PWR IN 21 DOUT7 20

https://www.envox.eu
Mixed I/O module for BB3+
Licensed under the TAPR Open Hardware License (www.tapr.org/OHL)
Envox d.o.o.
Sheet: /Voltage_current DACs/
File: Voltage_current_DACs.kicad_sch
Title: EEZ DIB MIO168+ module

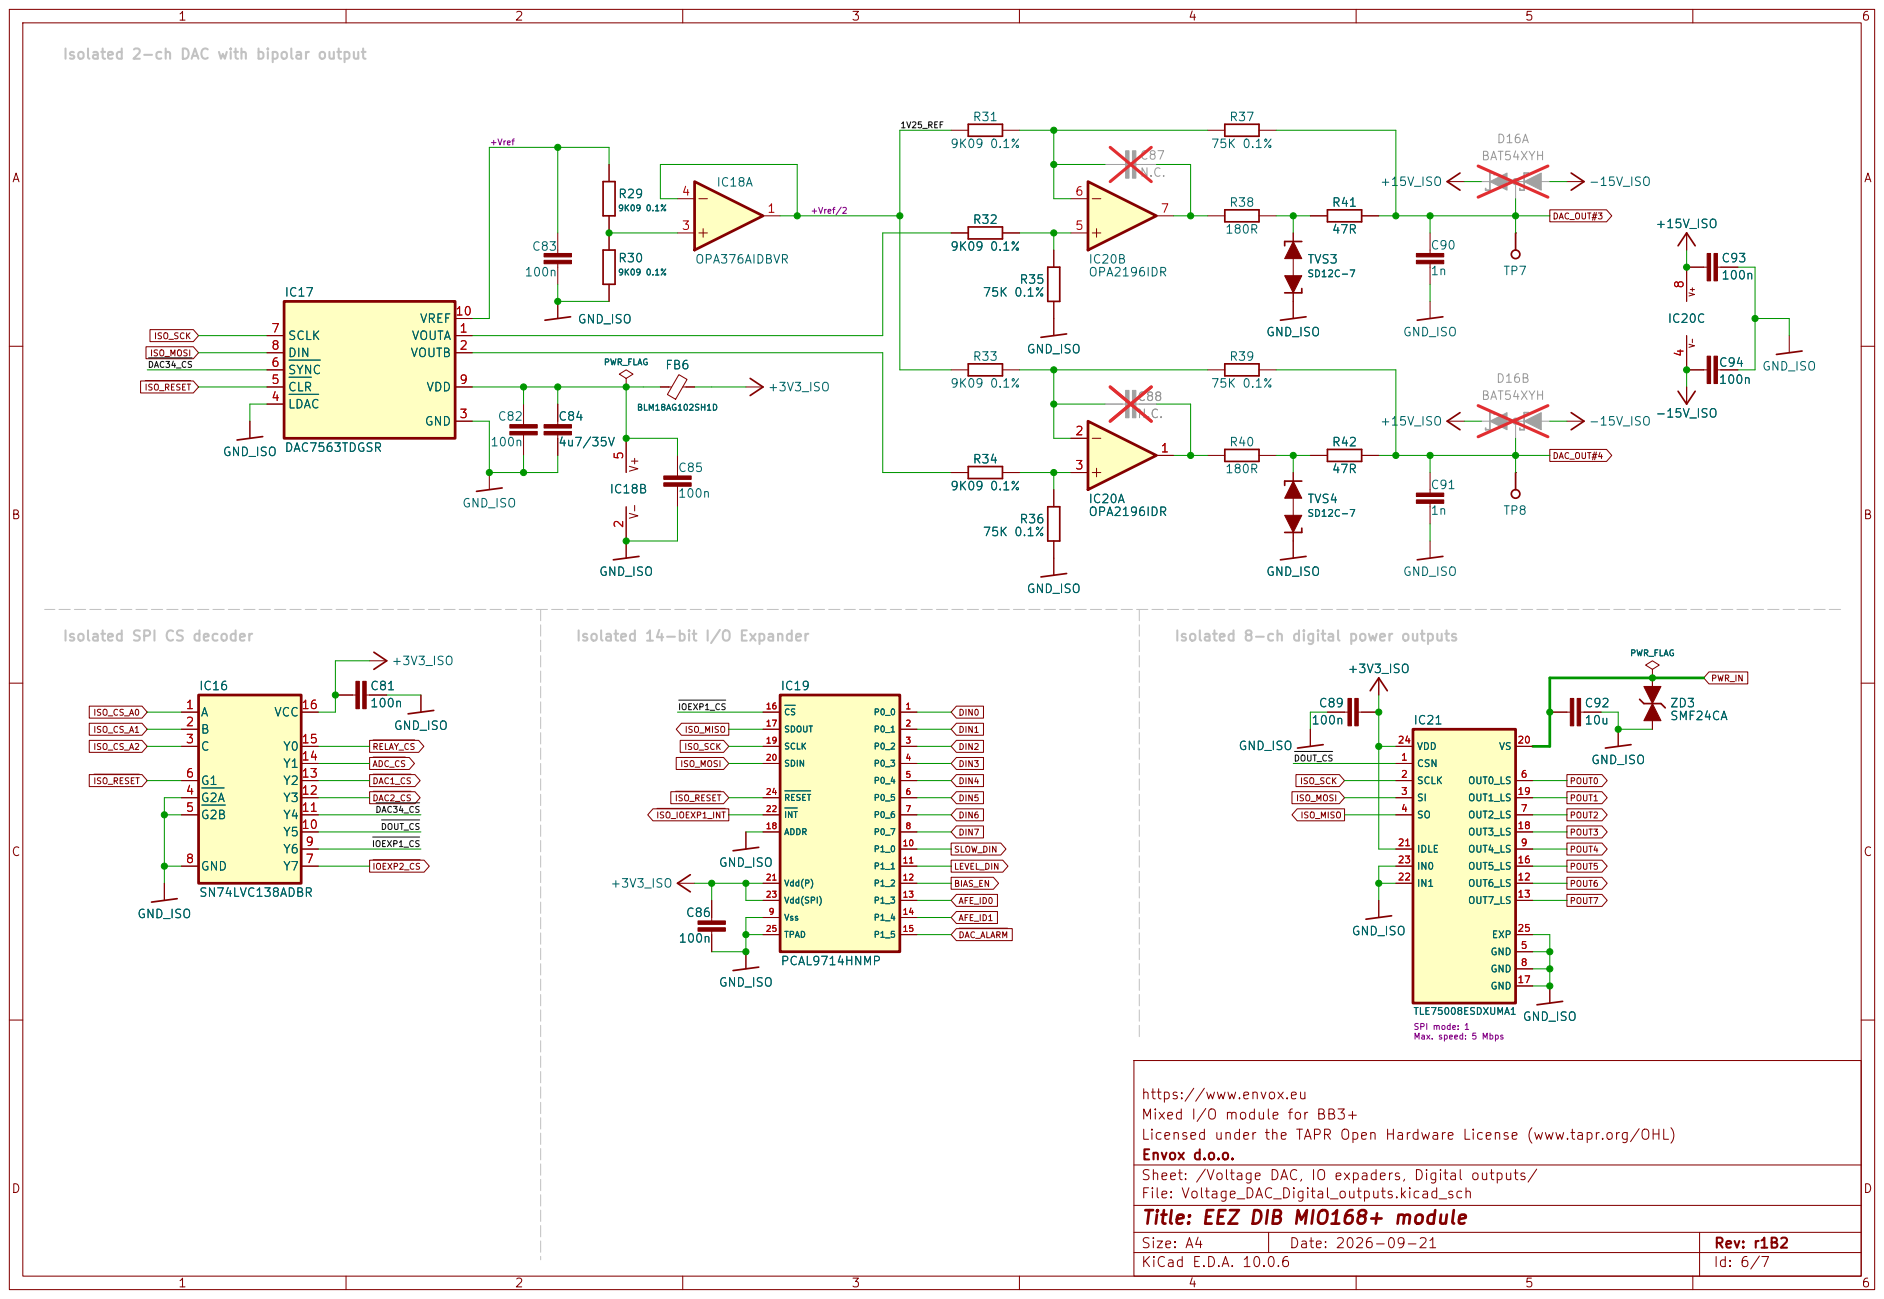
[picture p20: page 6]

Isolated SPI CS decoder

Isolated 8-ch digital power outputs

SPI mode: 1 Max. speed: 5 Mbps

https://www.envox.eu
Mixed I/O module for BB3+
Licensed under the TAPR Open Hardware License (www.tapr.org/OHL)
Envox d.o.o.
Sheet: /Voltage DAC, IO expaders, Digital outputs/
File: Voltage_DAC_Digital_outputs.kicad_sch
Title: EEZ DIB MIO168+ module

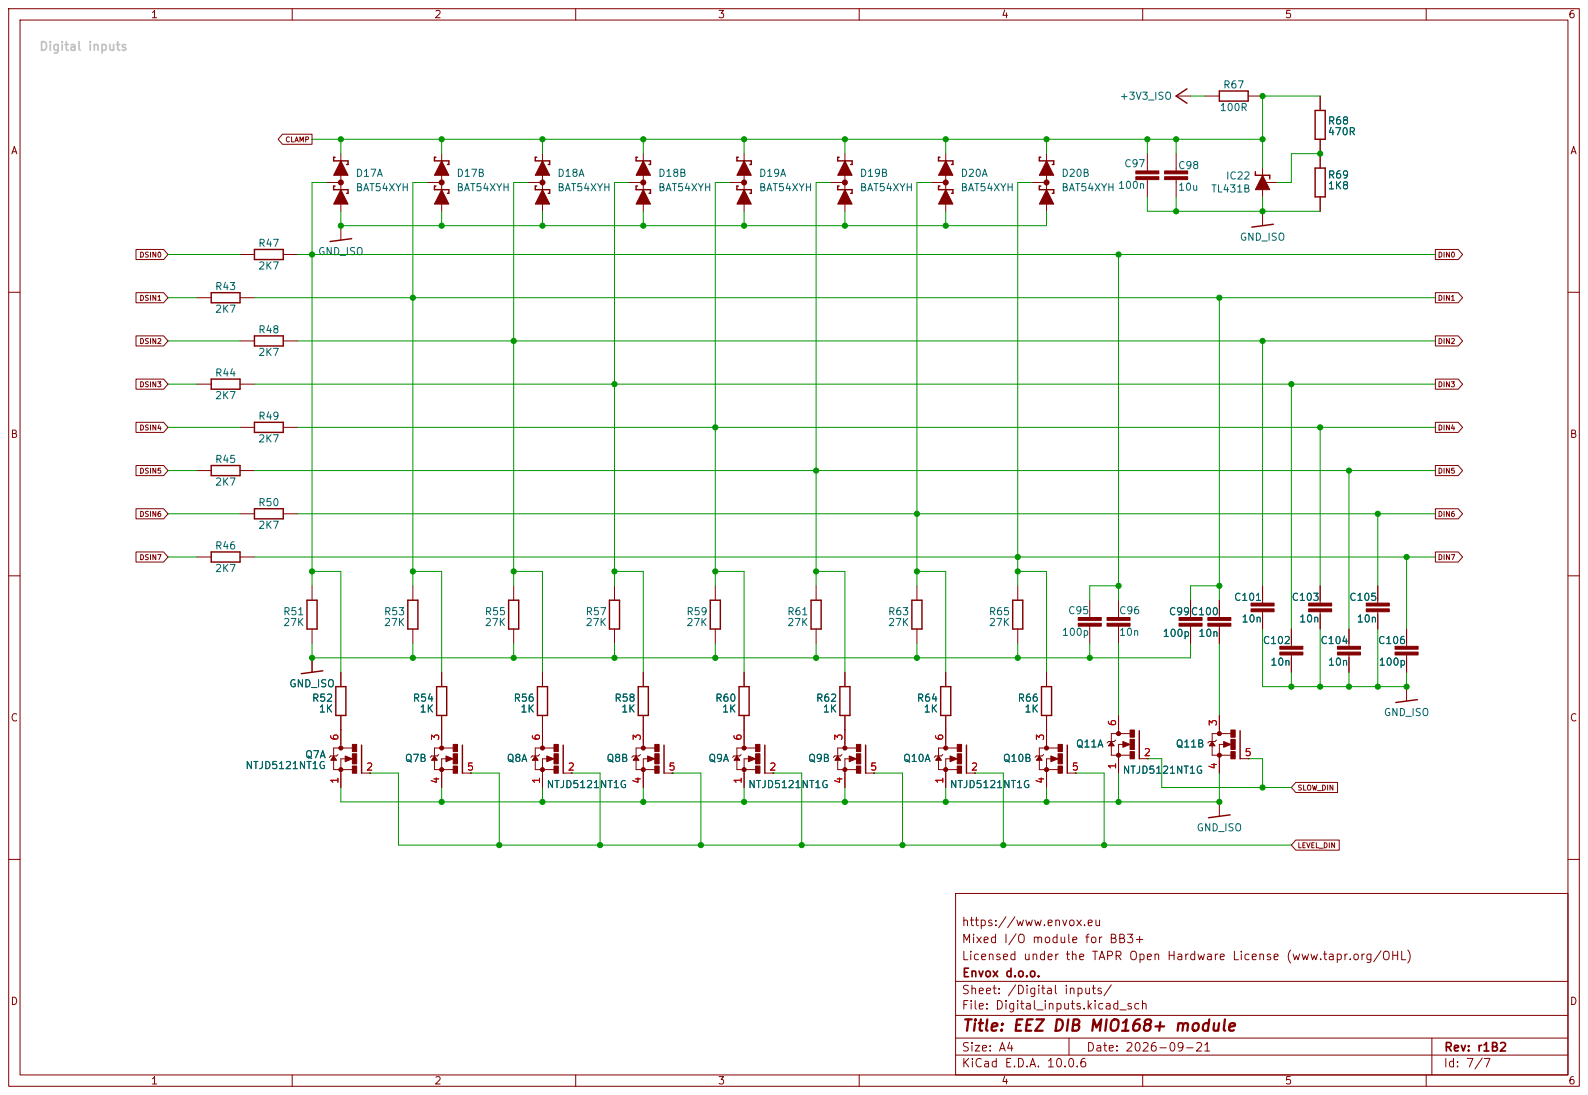
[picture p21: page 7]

https://www.envox.eu
Mixed I/O module for BB3+
Licensed under the TAPR Open Hardware License (www.tapr.org/OHL)
Envox d.o.o.
Sheet: /Digital inputs/
File: Digital_inputs.kicad_sch
Title: EEZ DIB MIO168+ module

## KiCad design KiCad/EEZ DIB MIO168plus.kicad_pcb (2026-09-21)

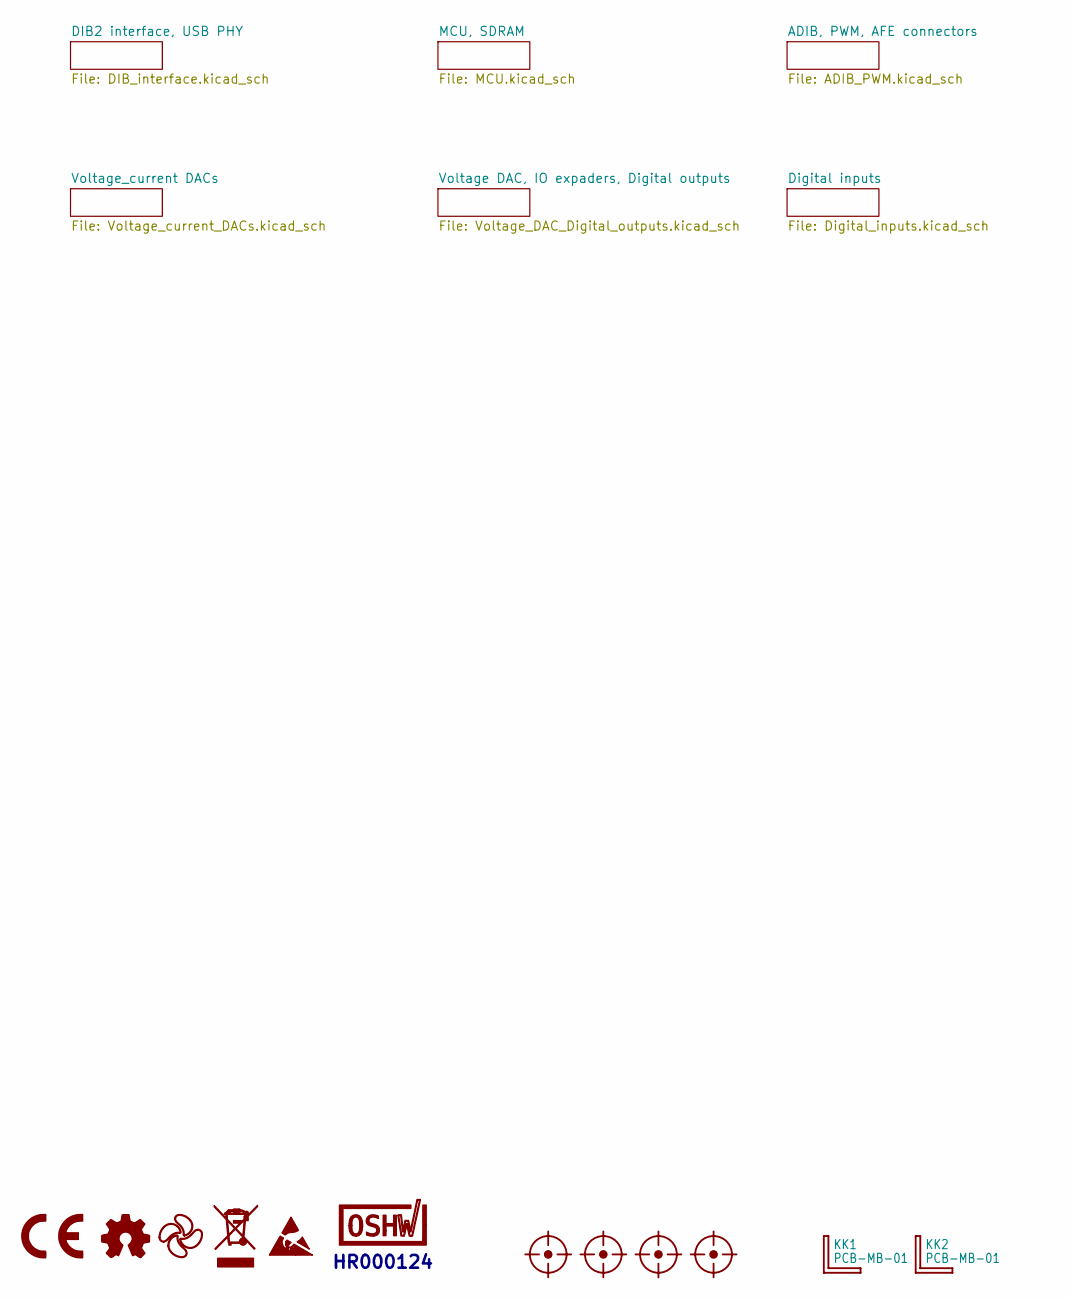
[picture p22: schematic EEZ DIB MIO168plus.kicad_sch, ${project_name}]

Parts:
FM1, FM2, FM3, FM4: FIDUCIAL_2; Fiducial_0.75mm_Mask1.5mm
KK1, KK2: PCB-MB-01; DigiKey RPC1760-ND
LOGO1: CE logo
LOGO2: Open hardware logo; Open HW logo
LOGO3: EEZ logo; EEZ logo (outline 6mm)
LOGO4: WEEE logo
LOGO5: ESD logo
LOGO7: OSHWA logo; OSHWA logo 6.6mm

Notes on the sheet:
HR000124

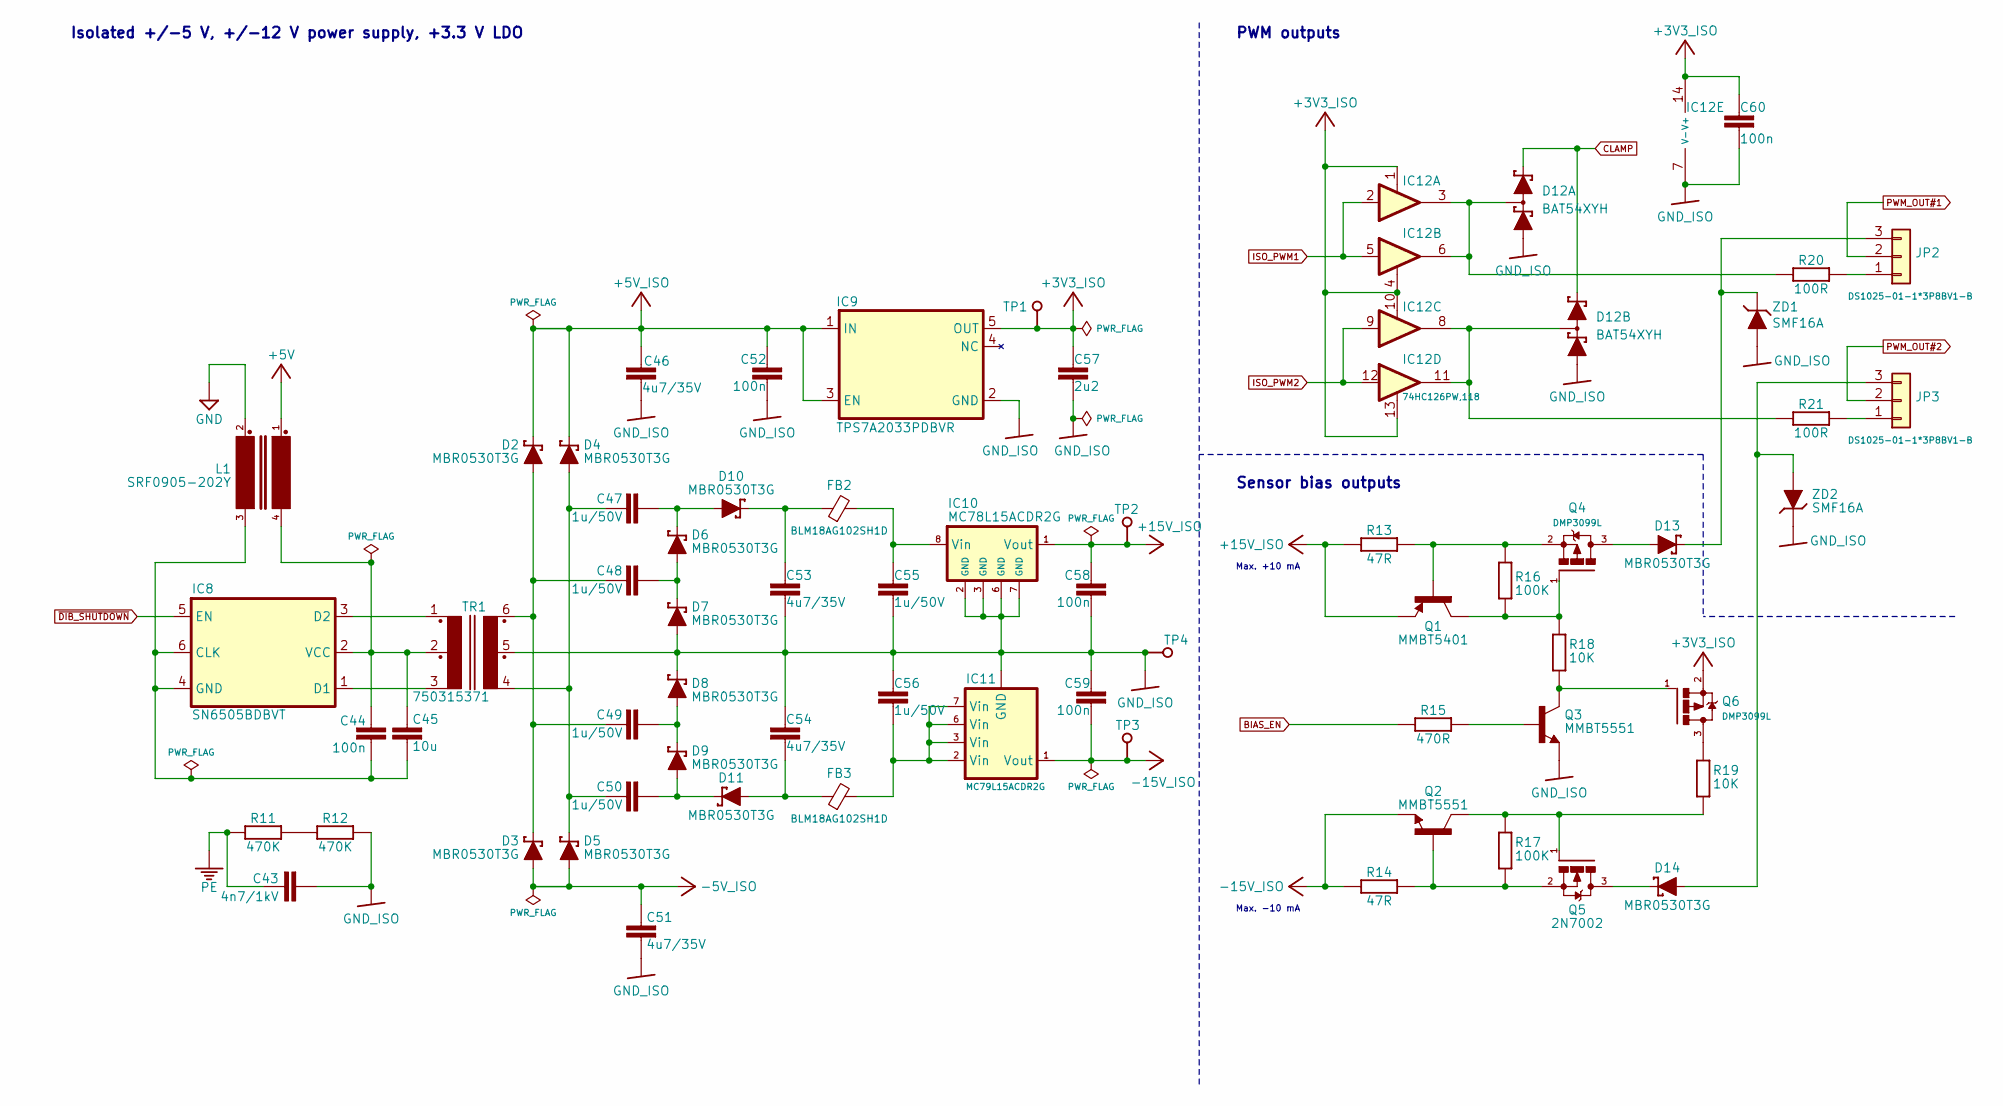
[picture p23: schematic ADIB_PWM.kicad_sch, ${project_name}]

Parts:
C43: 4n7/1kV; C_1206_3216Metric; DigiKey 732-12074-2-ND
C44, C52, C58, C59, C60: 100n; C_0603_1608Metric; DigiKey 490-4774-1-ND
C45: 10u; C_0805_2012Metric; DigiKey 490-5523-1-ND
C46, C51, C53, C54: 4u7/35V; C_0603_1608Metric; DigiKey 1276-6794-1-ND
C47, C48, C49, C50, C55, C56: 1u/50V; C_0603_1608Metric; DigiKey 1276-1860-1-ND
C57: 2u2; C_0603_1608Metric; DigiKey 490-12738-1-ND
D2, D3, D4, D5, D6, D7, D8, D9, D10, D11, D13, D14: MBR0530T3G; SOD123; DigiKey 863-MBR0530T3G
D12: BAT54XYH; SOP65P210X110-6N; DigiKey 1727-2723-1-ND
FB2, FB3: BLM18AG102SH1D; BEAD0603; DigiKey 490-7809-1-ND
IC8: SN6505BDBVT; DBV0006A_N; DigiKey 296-43154-2-ND
IC9: TPS7A2033PDBVR; DBV5; DigiKey 296-TPS7A2033PDBVRCT-ND
IC10: MC78L15ACDR2G; SOIC127P600X173-8N; DigiKey MC78L15ACDR2GOSDKR-ND
IC11: MC79L15ACDR2G; SOIC127P600X173-8N; DigiKey MC79L15ABDR2GOSDKR
IC12: 74HC126PW,118; PW(R-PDSO-G14); DigiKey 1727-6579-1-ND
JP2, JP3: DS1025-01-1*3P8BV1-B; ZL303-03P; DigiKey 952-1312-ND
L1: SRF0905-202Y; SRF0905; DigiKey SRF0905-202YCT-ND
Q1: MMBT5401; SOT23-BEC; DigiKey MMBT5401-FDICT-ND
Q2, Q3: MMBT5551; SOT23-BEC; DigiKey MMBT5551LT1GOSCT-ND
Q4, Q6: DMP3099L; SOT103P240X110-3N; DigiKey DMP3099L-13DICT-ND
Q5: 2N7002; SOT103P240X110-3N; DigiKey 2N7002LT1GOSCT-ND
R11, R12: 470K; R_0805_2012Metric; DigiKey A126370CT-ND
R13, R14: 47R; R_0603_1608Metric; DigiKey 13-RC0603FR-1347RLCT-ND
R15: 470R; R_0603_1608Metric; DigiKey 13-AC0603FR-7W470RLCT-ND
R16, R17: 100K; R_0603_1608Metric; DigiKey 311-100KHRCT-ND
R18, R19: 10K; R_0603_1608Metric; DigiKey 1712-CRGH0603F10KCT-ND
R20, R21: 100R; R_0603_1608Metric; DigiKey 13-RC0603FR-10100RLCT-ND
TP1, TP2, TP3: Test; Testhole 24_50mils
TP4: Test; TEST-5
TR1: 750315371; MURATA_78615; DigiKey 1297-1178-1-ND
ZD1, ZD2: SMF16A; SODFL3718X130N; DigiKey 4878-SMF16ATR-ND

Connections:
+3V3_ISO: C57.1, C60.2, IC9.5 (OUT), IC12.1 (EN), IC12.4 (EN), IC12.10 (EN), IC12.13 (EN), IC12.14 (V+), Q6.2 (S), TP1.1 (P$1_1); also elsewhere on the board
+5V: L1.1; also elsewhere on the board
+5V_ISO: C46.2, C52.1, D2.C, D4.C, IC9.1 (IN), IC9.3 (EN); also elsewhere on the board
+15V_ISO: C58.1, IC10.1 (Vout), Q1.E, R13.1, TP2.1 (P$1_1); also elsewhere on the board
-5V_ISO: C51.2, D3.A, D5.A; also elsewhere on the board
-15V_ISO: C59.2, IC11.1 (Vout), Q2.E, R14.1, TP3.1 (P$1_1); also elsewhere on the board
BIAS_EN: R15.2; also elsewhere on the board
CLAMP: D12.2 (K2), D12.5 (K3); also elsewhere on the board
GND: L1.2; also elsewhere on the board
GND_ISO: C43.2, C46.1, C51.1, C52.2, C53.2, C54.1, C55.1, C56.2, C57.2, C58.2, C59.1, C60.1, D7.A, D8.C, D12.1 (A1), D12.4 (A4), IC9.2 (GND), IC10.2 (GND), IC10.3 (GND), IC10.6 (GND), IC10.7 (GND), IC11.5 (GND), IC12.7 (V-), Q3.E, R12.2, TP4.1 (P$1_1), TR1.5, ZD1.C, ZD2.A; also elsewhere on the board
ISO_PWM1: IC12.2 (I), IC12.5 (I); also elsewhere on the board
ISO_PWM2: IC12.9 (I), IC12.12 (I); also elsewhere on the board
unnamed: C47.1, D6.C, D10.A
unnamed: C47.2, C50.2, D4.A, D5.C, TR1.4
unnamed: C48.1, D6.A, D7.C
unnamed: C48.2, C49.2, D2.A, D3.C, TR1.6
unnamed: C49.1, D8.A, D9.C
unnamed: C50.1, D9.A, D11.C
unnamed: C53.1, D10.C, FB2.1
unnamed: C54.2, D11.A, FB3.1
unnamed: C56.1, FB3.2, IC11.2 (Vin), IC11.3 (Vin), IC11.6 (Vin), IC11.7 (Vin)
unnamed: D12.6 (K1A2), IC12.3 (O), IC12.6 (O), R20.2
unnamed: D12.3 (A3K4), IC12.8 (O), IC12.11 (O), R21.2
unnamed: C44.2, C45.1, IC8.4 (GND), IC8.6 (CLK), L1.3
unnamed: IC8.1 (D1), TR1.3
unnamed: IC8.3 (D2), TR1.1
unnamed: C44.1, C45.2, IC8.2 (VCC), L1.4, TR1.2
unnamed: C55.2, FB2.2, IC10.8 (Vin)
unnamed: JP2.1, R20.1
unnamed: D13.C, JP2.3, ZD1.A
unnamed: JP3.1, R21.1
unnamed: D14.A, JP3.3, ZD2.C
unnamed: Q3.B, R15.1
unnamed: D13.A, Q4.3 (D)
unnamed: Q1.C, Q4.1 (G), R16.2, R18.1
unnamed: Q1.B, Q4.2 (S), R13.2, R16.1
unnamed: D14.C, Q5.3 (D)
unnamed: Q2.C, Q5.1 (G), R17.1, R19.2
unnamed: Q2.B, Q5.2 (S), R14.2, R17.2
unnamed: Q6.3 (D), R19.1
unnamed: Q3.C, Q6.1 (G), R18.2
unnamed: R11.2, R12.1
PE: C43.1, R11.1; also elsewhere on the board
PWM_OUT#1: JP2.2; also elsewhere on the board
PWM_OUT#2: JP3.2; also elsewhere on the board
~DIB_SHUTDOWN: IC8.5 (EN); also elsewhere on the board

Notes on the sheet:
Max. -10 mA
Max. +10 mA
Sensor bias outputs
PWM outputs
Isolated +/-5 V, +/-12 V power supply, +3.3 V LDO

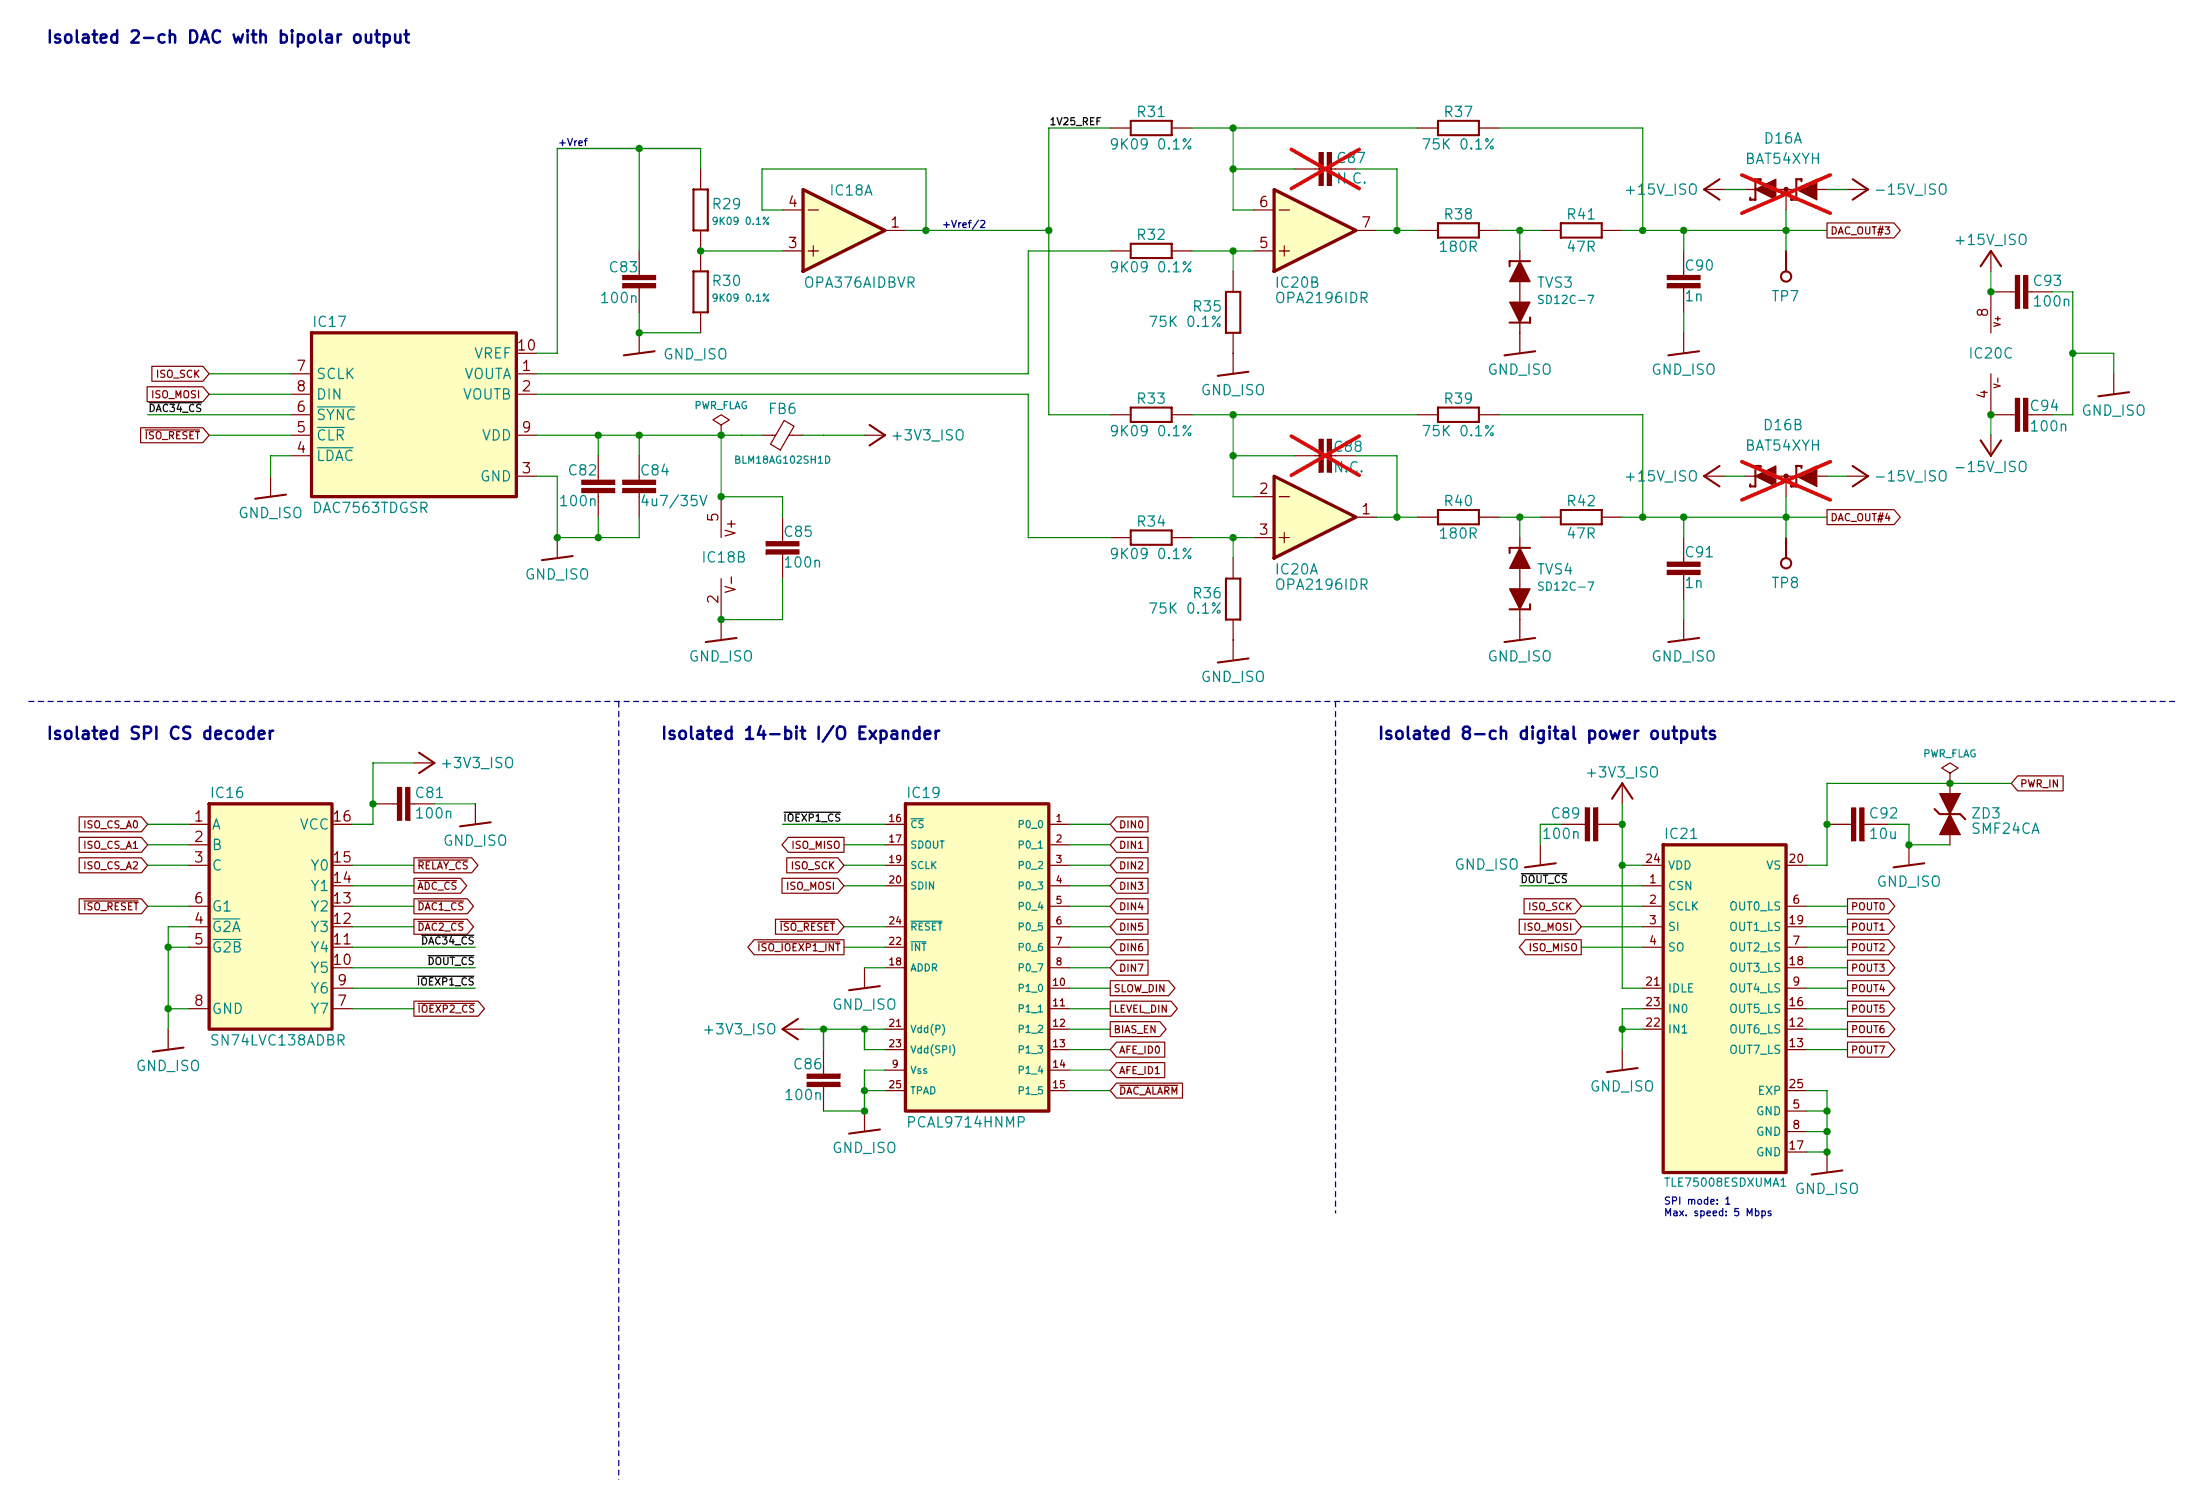
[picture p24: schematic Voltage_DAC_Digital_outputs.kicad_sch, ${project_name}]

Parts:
C81, C82, C83, C85, C86, C89, C93, C94: 100n; C_0603_1608Metric; DigiKey 490-4774-1-ND
C84: 4u7/35V; C_0603_1608Metric; DigiKey 1276-6794-1-ND
C87, C88: N.C.; C_0603_1608Metric; not fitted
C90, C91: 1n; C_0603_1608Metric; DigiKey 1276-1018-2-ND
C92: 10u; C_0805_2012Metric; DigiKey 490-5523-1-ND
D16: BAT54XYH; SOP65P210X110-6N; DigiKey 1727-2723-1-ND; not fitted
FB6: BLM18AG102SH1D; BEAD0603; DigiKey 490-7809-1-ND
IC16: SN74LVC138ADBR; DB16; DigiKey 296-8460-1-ND
IC17: DAC7563TDGSR; DGS10; DigiKey 296-43287-1-ND
IC18: OPA376AIDBVR; SOT23-5L_STM; DigiKey 296-39130-2-ND
IC19: PCAL9714HNMP; QFN50P400X400X100-25N; DigiKey 568-PCAL9714HNMPCT-ND
IC20: OPA2196IDR; SOIC127P600X173-8N; DigiKey 296-48159-1-ND
IC21: TLE75008ESDXUMA1; SOP65P600X115-25N; DigiKey 448-TLE75008ESDXUMA1CT-ND
R29, R30, R31, R32, R33, R34: 9K09 0.1%; R_0603_1608Metric; DigiKey YAG4788CT-ND
R35, R36, R37, R39: 75K 0.1%; R_0603_1608Metric; DigiKey YAG1730CT-ND
R38, R40: 180R; R_0603_1608Metric; DigiKey 13-RC0603FR-13180RLCT-ND
R41, R42: 47R; R_0603_1608Metric; DigiKey 13-RC0603FR-1347RLCT-ND
TP7, TP8: Test; Testhole 24_50mils
TVS3, TVS4: SD12C-7; SOD-323_PESD; DigiKey 31-SD12C-7CT-ND
ZD3: SMF24CA; SODFL3718X130N; DigiKey 4878-SMF24CADKR-ND

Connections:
+3V3_ISO: C81.1, C86.1, C89.2, FB6.2, IC16.16 (VCC), IC19.21 (Vdd(P)), IC19.23 (Vdd(SPI)), IC21.21 (IDLE), IC21.24 (VDD); also elsewhere on the board
+15V_ISO: C93.1, D16.2 (K2), D16.5 (K3), IC20.8 (V+); also elsewhere on the board
-15V_ISO: C94.1, D16.1 (A1), D16.4 (A4), IC20.4 (V-); also elsewhere on the board
/Voltage DAC, IO expaders, Digital outputs/1V25_REF: IC18.1 (OUT), IC18.4 (-IN), R31.2, R33.2
/Voltage DAC, IO expaders, Digital outputs/~DAC34_CS: IC16.11 (Y4), IC17.6 (~SYNC)
/Voltage DAC, IO expaders, Digital outputs/~DOUT_CS: IC16.10 (Y5), IC21.1 (CSN)
/Voltage DAC, IO expaders, Digital outputs/~IOEXP1_CS: IC16.9 (Y6), IC19.16 (~CS)
AFE_ID0: IC19.13 (P1_3); also elsewhere on the board
AFE_ID1: IC19.14 (P1_4); also elsewhere on the board
BIAS_EN: IC19.12 (P1_2); also elsewhere on the board
DAC_OUT#3: C90.1, D16.6 (K1A2), R37.1, R41.2, TP7.1 (P$1_1); also elsewhere on the board
DAC_OUT#4: C91.1, D16.3 (A3K4), R39.1, R42.2, TP8.1 (P$1_1); also elsewhere on the board
DIN0: IC19.1 (P0_0); also elsewhere on the board
DIN1: IC19.2 (P0_1); also elsewhere on the board
DIN2: IC19.3 (P0_2); also elsewhere on the board
DIN3: IC19.4 (P0_3); also elsewhere on the board
DIN4: IC19.5 (P0_4); also elsewhere on the board
DIN5: IC19.6 (P0_5); also elsewhere on the board
DIN6: IC19.7 (P0_6); also elsewhere on the board
DIN7: IC19.8 (P0_7); also elsewhere on the board
GND_ISO: C81.2, C82.2, C83.1, C84.1, C85.2, C86.2, C89.1, C90.2, C91.2, C92.1, C93.2, C94.2, IC16.4 (~G2A), IC16.5 (~G2B), IC16.8 (GND), IC17.3 (GND), IC17.4 (~LDAC), IC18.2 (V-), IC19.9 (Vss), IC19.18 (ADDR), IC19.25 (TPAD), IC21.5 (GND), IC21.8 (GND), IC21.17 (GND), IC21.22 (IN1), IC21.23 (IN0), IC21.25 (EXP), R30.2, R35.2, R36.2, TVS3.C1 (1), TVS4.C1 (1), ZD3.C; also elsewhere on the board
ISO_CS_A0: IC16.1 (A); also elsewhere on the board
ISO_CS_A1: IC16.2 (B); also elsewhere on the board
ISO_CS_A2: IC16.3 (C); also elsewhere on the board
ISO_MISO: IC19.17 (SDOUT), IC21.4 (SO); also elsewhere on the board
ISO_MOSI: IC17.8 (DIN), IC19.20 (SDIN), IC21.3 (SI); also elsewhere on the board
ISO_SCK: IC17.7 (SCLK), IC19.19 (SCLK), IC21.2 (SCLK); also elsewhere on the board
LEVEL_DIN: IC19.11 (P1_1); also elsewhere on the board
unnamed: C82.1, C84.2, C85.1, FB6.1, IC17.9 (VDD), IC18.5 (V+)
unnamed: IC17.1 (VOUTA), R32.2
unnamed: IC17.2 (VOUTB), R34.2
unnamed: C83.2, IC17.10 (VREF), R29.1
unnamed: IC18.3 (+IN), R29.2, R30.1
unnamed: IC20.3 (+IN), R34.1, R36.1
unnamed: C88.1, IC20.2 (-IN), R33.1, R39.2
unnamed: C88.2, IC20.1 (OUT), R40.1
unnamed: IC20.5 (+IN), R32.1, R35.1
unnamed: C87.1, IC20.6 (-IN), R31.1, R37.2
unnamed: C87.2, IC20.7 (OUT), R38.1
unnamed: R38.2, R41.1, TVS3.C2 (2)
unnamed: R40.2, R42.1, TVS4.C2 (2)
POUT0: IC21.6 (OUT0_LS); also elsewhere on the board
POUT1: IC21.19 (OUT1_LS); also elsewhere on the board
POUT2: IC21.7 (OUT2_LS); also elsewhere on the board
POUT3: IC21.18 (OUT3_LS); also elsewhere on the board
POUT4: IC21.9 (OUT4_LS); also elsewhere on the board
POUT5: IC21.16 (OUT5_LS); also elsewhere on the board
POUT6: IC21.12 (OUT6_LS); also elsewhere on the board
POUT7: IC21.13 (OUT7_LS); also elsewhere on the board
PWR_IN: C92.2, IC21.20 (VS), ZD3.A; also elsewhere on the board
SLOW_DIN: IC19.10 (P1_0); also elsewhere on the board
~ADC_CS: IC16.14 (Y1); also elsewhere on the board
~DAC1_CS: IC16.13 (Y2); also elsewhere on the board
~DAC2_CS: IC16.12 (Y3); also elsewhere on the board
~DAC_ALARM: IC19.15 (P1_5); also elsewhere on the board
~IOEXP2_CS: IC16.7 (Y7); also elsewhere on the board
~ISO_IOEXP1_INT: IC19.22 (~INT); also elsewhere on the board
~ISO_RESET: IC16.6 (G1), IC17.5 (~CLR), IC19.24 (~RESET); also elsewhere on the board
~RELAY_CS: IC16.15 (Y0); also elsewhere on the board

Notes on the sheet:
SPI mode: 1 Max. speed: 5 Mbps
+Vref
Isolated SPI CS decoder
+Vref/2
Isolated 8-ch digital power outputs
Isolated 2-ch DAC with bipolar output
Isolated 14-bit I/O Expander

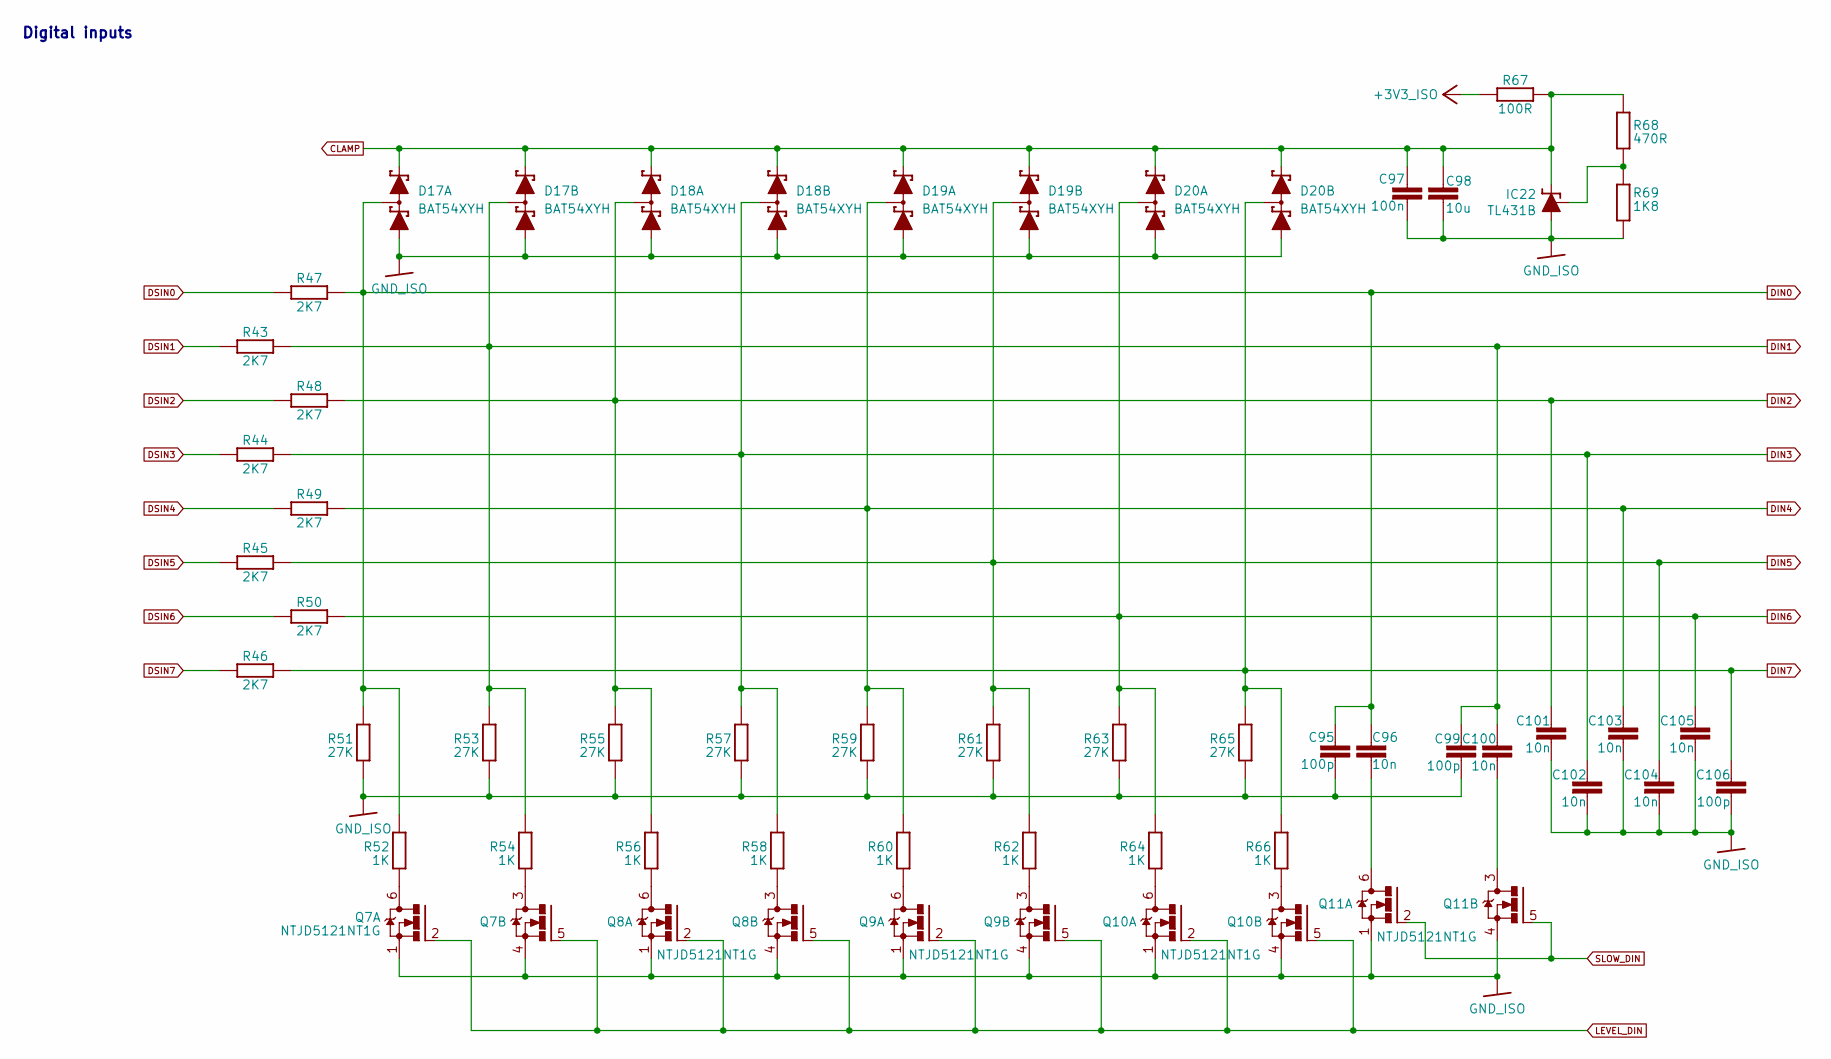
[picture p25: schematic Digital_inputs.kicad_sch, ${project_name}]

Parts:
C95, C99, C106: 100p; C_0603_1608Metric; DigiKey 490-11153-1-ND
C96, C100, C101, C102, C103, C104, C105: 10n; C_0603_1608Metric; DigiKey 1276-1009-1-ND
C97: 100n; C_0603_1608Metric; DigiKey 490-4774-1-ND
C98: 10u; C_0805_2012Metric; DigiKey 490-5523-1-ND
D17, D18, D19, D20: BAT54XYH; SOP65P210X110-6N; DigiKey 1727-2723-1-ND
IC22: TL431B; SOT103P240X110-3N; DigiKey 296-17332-1-ND
Q7, Q8, Q9, Q10, Q11: NTJD5121NT1G; SC88; DigiKey NTJD5121NT1GOSCT-ND
R43, R44, R45, R46, R47, R48, R49, R50: 2K7; R_1206_3216Metric; DigiKey 311-2.70KFRCT-ND
R51, R53, R55, R57, R59, R61, R63, R65: 27K; R_0603_1608Metric; DigiKey 311-27.0KHRCT-ND
R52, R54, R56, R58, R60, R62, R64, R66: 1K; R_0603_1608Metric; DigiKey 13-RC0603FR-131KLCT-ND
R67: 100R; R_0603_1608Metric; DigiKey 13-RC0603FR-10100RLCT-ND
R68: 470R; R_0603_1608Metric; DigiKey 13-AC0603FR-7W470RLCT-ND
R69: 1K8; R_0603_1608Metric; DigiKey 13-RC0603FR-131K8LCT-ND

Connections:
+3V3_ISO: R67.1; also elsewhere on the board
CLAMP: C97.1, C98.1, D17.2 (K2), D17.5 (K3), D18.2 (K2), D18.5 (K3), D19.2 (K2), D19.5 (K3), D20.2 (K2), D20.5 (K3), IC22.1 (C), R67.2, R68.1; also elsewhere on the board
DIN0: C95.1, C96.1, D17.6 (K1A2), R47.2, R51.2, R52.1; also elsewhere on the board
DIN1: C99.1, C100.1, D17.3 (A3K4), R43.2, R53.2, R54.1; also elsewhere on the board
DIN2: C101.1, D18.6 (K1A2), R48.2, R55.2, R56.1; also elsewhere on the board
DIN3: C102.1, D18.3 (A3K4), R44.2, R57.2, R58.1; also elsewhere on the board
DIN4: C103.1, D19.6 (K1A2), R49.2, R59.2, R60.1; also elsewhere on the board
DIN5: C104.1, D19.3 (A3K4), R45.2, R61.2, R62.1; also elsewhere on the board
DIN6: C105.1, D20.6 (K1A2), R50.2, R63.2, R64.1; also elsewhere on the board
DIN7: C106.1, D20.3 (A3K4), R46.2, R65.2, R66.1; also elsewhere on the board
DSIN0: R47.1; also elsewhere on the board
DSIN1: R43.1; also elsewhere on the board
DSIN2: R48.1; also elsewhere on the board
DSIN3: R44.1; also elsewhere on the board
DSIN4: R49.1; also elsewhere on the board
DSIN5: R45.1; also elsewhere on the board
DSIN6: R50.1; also elsewhere on the board
DSIN7: R46.1; also elsewhere on the board
GND_ISO: C95.2, C97.2, C98.2, C99.2, C101.2, C102.2, C103.2, C104.2, C105.2, C106.2, D17.1 (A1), D17.4 (A4), D18.1 (A1), D18.4 (A4), D19.1 (A1), D19.4 (A4), D20.1 (A1), D20.4 (A4), IC22.3 (A), Q7.1 (S), Q7.4 (S), Q8.1 (S), Q8.4 (S), Q9.1 (S), Q9.4 (S), Q10.1 (S), Q10.4 (S), Q11.1 (S), Q11.4 (S), R51.1, R53.1, R55.1, R57.1, R59.1, R61.1, R63.1, R65.1, R69.2; also elsewhere on the board
LEVEL_DIN: Q7.2 (G), Q7.5 (G), Q8.2 (G), Q8.5 (G), Q9.2 (G), Q9.5 (G), Q10.2 (G), Q10.5 (G); also elsewhere on the board
unnamed: IC22.2 (R), R68.2, R69.1
unnamed: Q7.6 (D), R52.2
unnamed: Q7.3 (D), R54.2
unnamed: Q8.6 (D), R56.2
unnamed: Q8.3 (D), R58.2
unnamed: Q9.6 (D), R60.2
unnamed: Q9.3 (D), R62.2
unnamed: Q10.6 (D), R64.2
unnamed: Q10.3 (D), R66.2
unnamed: C96.2, Q11.6 (D)
unnamed: C100.2, Q11.3 (D)
SLOW_DIN: Q11.2 (G), Q11.5 (G); also elsewhere on the board

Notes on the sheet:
Digital inputs

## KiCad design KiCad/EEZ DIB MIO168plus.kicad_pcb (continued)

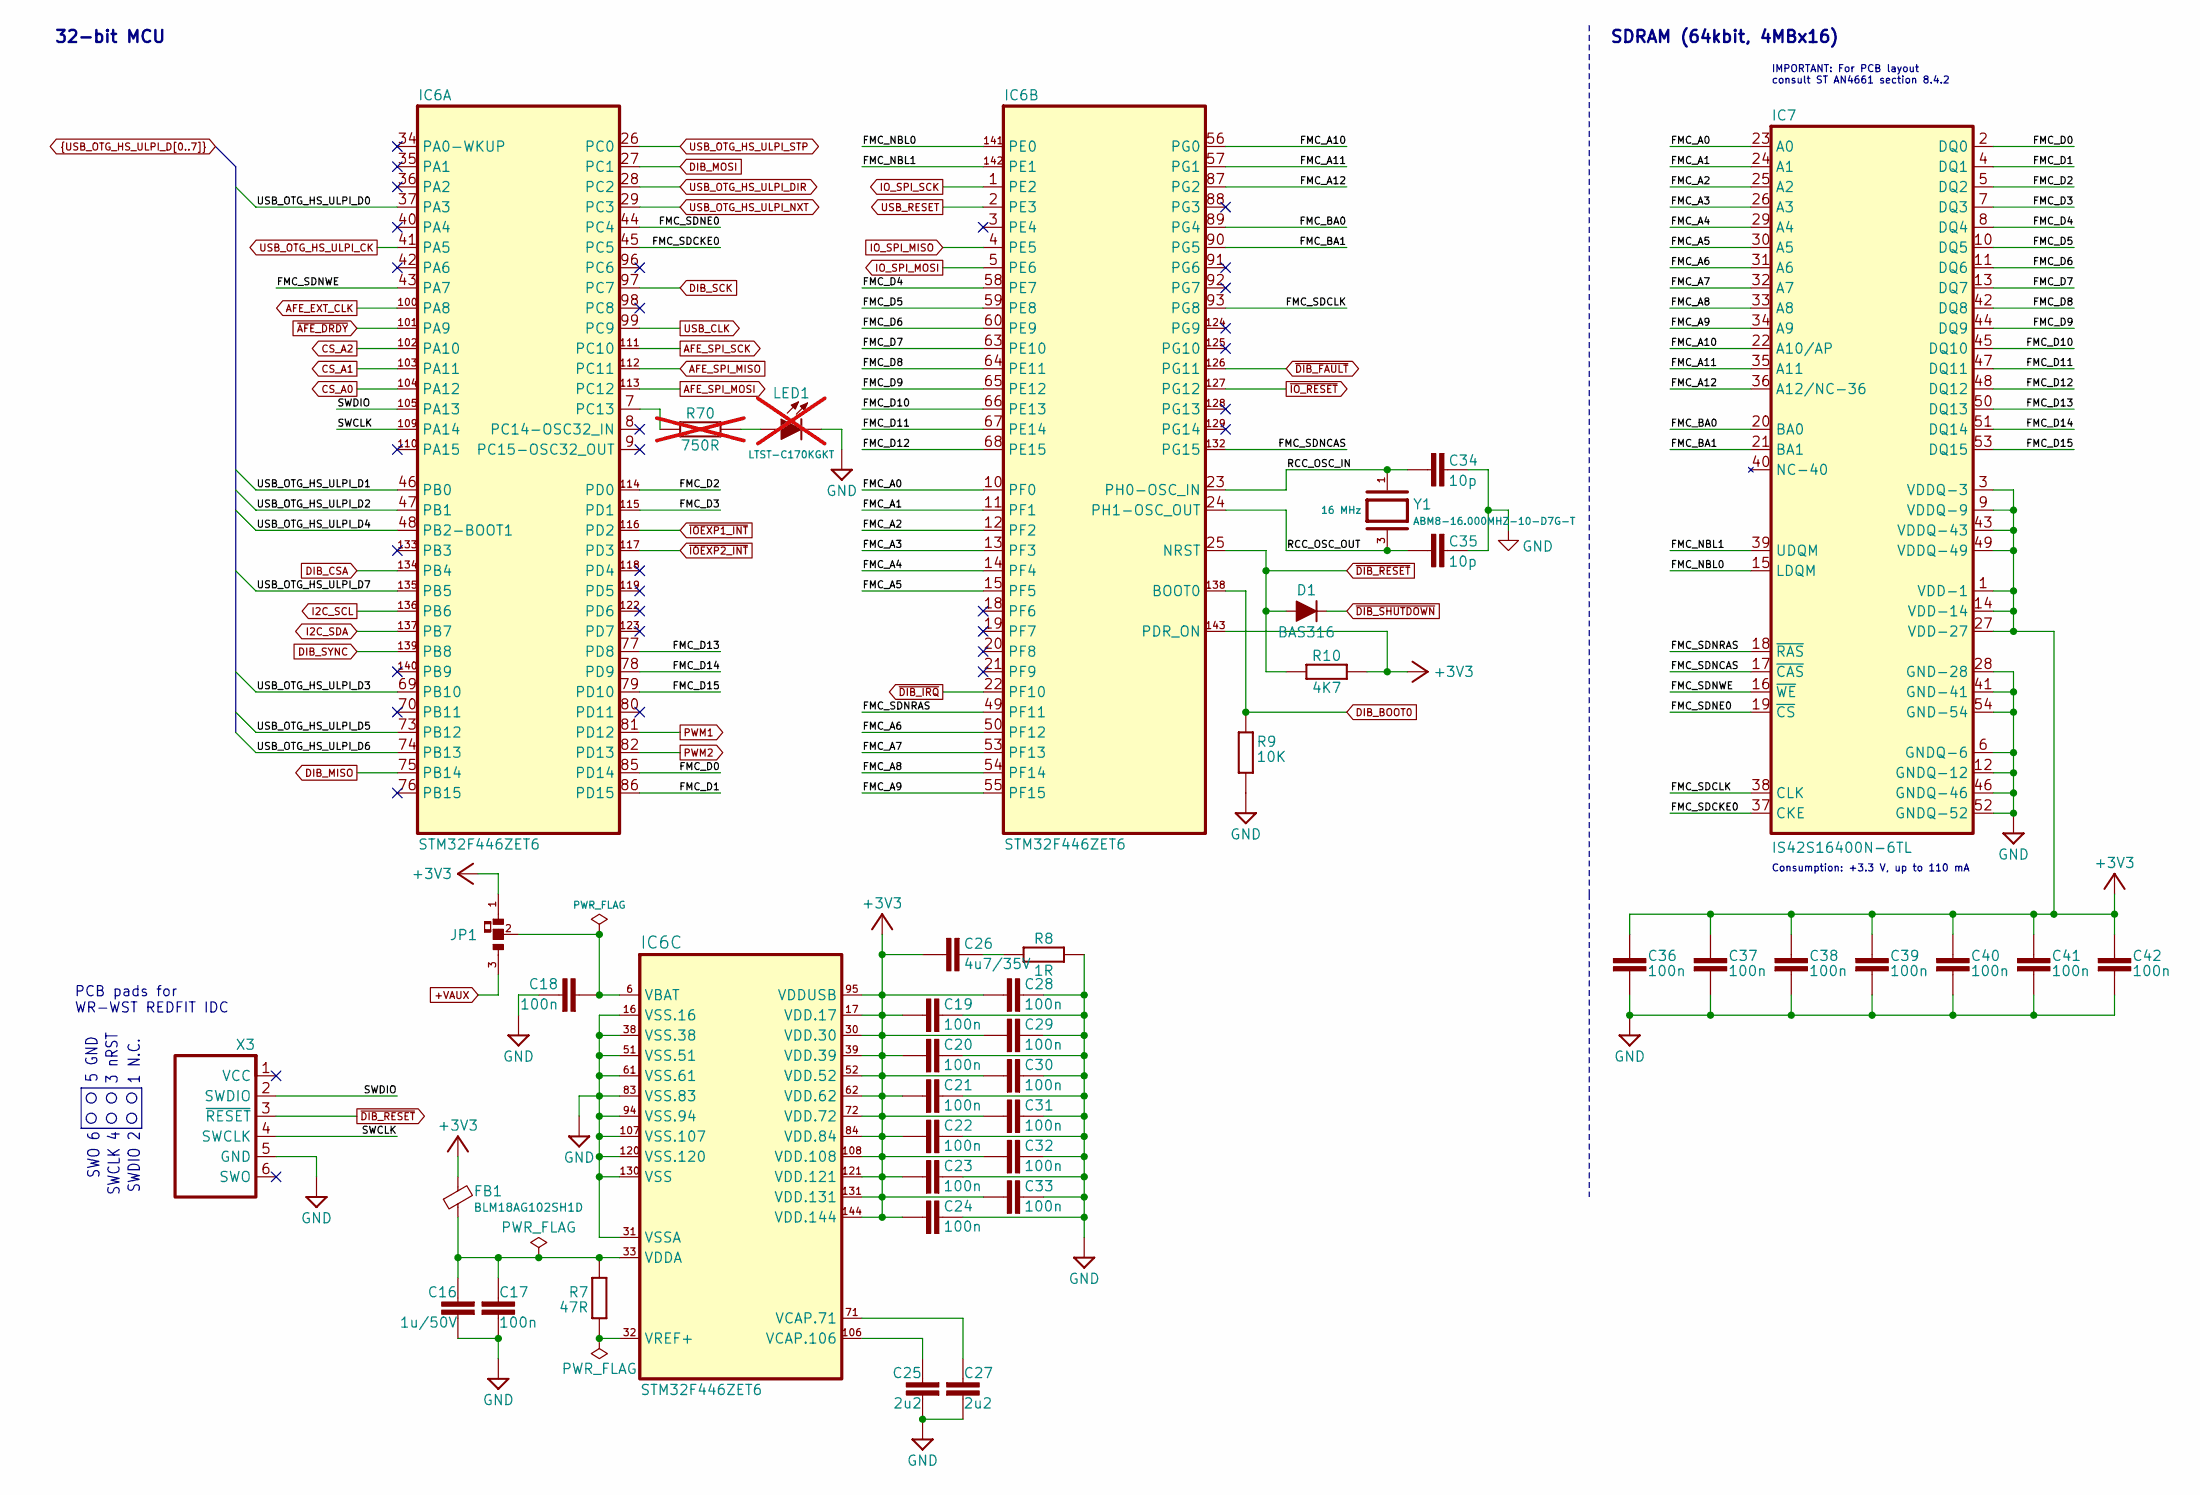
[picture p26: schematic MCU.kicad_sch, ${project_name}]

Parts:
C16: 1u/50V; C_0603_1608Metric; DigiKey 1276-1860-1-ND
C17, C18, C19, C20, C21, C22, C23, C24, C28, C29, C30, C31, C32, C33, C36, C37, C38, C39, C40, C41, C42: 100n; C_0603_1608Metric; DigiKey 490-4774-1-ND
C25, C27: 2u2; C_0603_1608Metric; DigiKey 490-12738-1-ND
C26: 4u7/35V; C_0603_1608Metric; DigiKey 1276-6794-1-ND
C34, C35: 10p; C_0603_1608Metric; DigiKey 1276-1069-1-ND
D1: BAS316; SOD-323_1P8X1P35_ONS-M; DigiKey 1727-7370-1-ND
FB1: BLM18AG102SH1D; BEAD0603; DigiKey 490-7809-1-ND
IC6: STM32F446ZET6; LQFP-144_20X20MM; DigiKey 497-15374-ND
IC7: IS42S16400N-6TL; TSOPII-54; DigiKey 1450-1260-ND
JP1: JP3 shorted with 0R (0603)
LED1: LTST-C170KGKT; LED_LTST-C170KGKT_LTO-L; DigiKey 160-1414-2-ND; not fitted
R7: 47R; R_0603_1608Metric; DigiKey 13-RC0603FR-1347RLCT-ND
R8: 1R; R_0603_1608Metric; DigiKey 118-CHP0603QFW-1R00ELFCT-ND
R9: 10K; R_0603_1608Metric; DigiKey 1712-CRGH0603F10KCT-ND
R10: 4K7; R_0603_1608Metric; DigiKey 13-RC0603FR-134K7LTR-ND
R70: 750R; R_0603_1608Metric; not fitted
X3: WR-WST_490107670612_DEBUG
Y1: ABM8-16.000MHZ-10-D7G-T; XTAL_403C11A24M00000; DigiKey 535-14383-1-ND

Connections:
+3V3: C19.1, C20.1, C21.1, C22.1, C23.1, C24.1, C26.1, C28.1, C29.1, C30.1, C31.1, C32.1, C33.1, C36.1, C37.1, C38.1, C39.1, C40.1, C41.1, C42.1, FB1.2, IC6.17 (VDD.17), IC6.30 (VDD.30), IC6.39 (VDD.39), IC6.52 (VDD.52), IC6.62 (VDD.62), IC6.72 (VDD.72), IC6.84 (VDD.84), IC6.95 (VDDUSB), IC6.108 (VDD.108), IC6.121 (VDD.121), IC6.131 (VDD.131), IC6.143 (PDR_ON), IC6.144 (VDD.144), IC7.1 (VDD-1), IC7.3 (VDDQ-3), IC7.9 (VDDQ-9), IC7.14 (VDD-14), IC7.27 (VDD-27), IC7.43 (VDDQ-43), IC7.49 (VDDQ-49), JP1.1, R10.2; also elsewhere on the board
+VAUX: JP1.3; also elsewhere on the board
/MCU, SDRAM/FMC_A0: IC6.10 (PF0), IC7.23 (A0)
/MCU, SDRAM/FMC_A1: IC6.11 (PF1), IC7.24 (A1)
/MCU, SDRAM/FMC_A2: IC6.12 (PF2), IC7.25 (A2)
/MCU, SDRAM/FMC_A3: IC6.13 (PF3), IC7.26 (A3)
/MCU, SDRAM/FMC_A4: IC6.14 (PF4), IC7.29 (A4)
/MCU, SDRAM/FMC_A5: IC6.15 (PF5), IC7.30 (A5)
/MCU, SDRAM/FMC_A6: IC6.50 (PF12), IC7.31 (A6)
/MCU, SDRAM/FMC_A7: IC6.53 (PF13), IC7.32 (A7)
/MCU, SDRAM/FMC_A8: IC6.54 (PF14), IC7.33 (A8)
/MCU, SDRAM/FMC_A9: IC6.55 (PF15), IC7.34 (A9)
/MCU, SDRAM/FMC_A10: IC6.56 (PG0), IC7.22 (A10/AP)
/MCU, SDRAM/FMC_A11: IC6.57 (PG1), IC7.35 (A11)
/MCU, SDRAM/FMC_A12: IC6.87 (PG2), IC7.36 (A12/NC-36)
/MCU, SDRAM/FMC_BA0: IC6.89 (PG4), IC7.20 (BA0)
/MCU, SDRAM/FMC_BA1: IC6.90 (PG5), IC7.21 (BA1)
/MCU, SDRAM/FMC_D0: IC6.85 (PD14), IC7.2 (DQ0)
/MCU, SDRAM/FMC_D1: IC6.86 (PD15), IC7.4 (DQ1)
/MCU, SDRAM/FMC_D2: IC6.114 (PD0), IC7.5 (DQ2)
/MCU, SDRAM/FMC_D3: IC6.115 (PD1), IC7.7 (DQ3)
/MCU, SDRAM/FMC_D4: IC6.58 (PE7), IC7.8 (DQ4)
/MCU, SDRAM/FMC_D5: IC6.59 (PE8), IC7.10 (DQ5)
/MCU, SDRAM/FMC_D6: IC6.60 (PE9), IC7.11 (DQ6)
/MCU, SDRAM/FMC_D7: IC6.63 (PE10), IC7.13 (DQ7)
/MCU, SDRAM/FMC_D8: IC6.64 (PE11), IC7.42 (DQ8)
/MCU, SDRAM/FMC_D9: IC6.65 (PE12), IC7.44 (DQ9)
/MCU, SDRAM/FMC_D10: IC6.66 (PE13), IC7.45 (DQ10)
/MCU, SDRAM/FMC_D11: IC6.67 (PE14), IC7.47 (DQ11)
/MCU, SDRAM/FMC_D12: IC6.68 (PE15), IC7.48 (DQ12)
/MCU, SDRAM/FMC_D13: IC6.77 (PD8), IC7.50 (DQ13)
/MCU, SDRAM/FMC_D14: IC6.78 (PD9), IC7.51 (DQ14)
/MCU, SDRAM/FMC_D15: IC6.79 (PD10), IC7.53 (DQ15)
/MCU, SDRAM/FMC_NBL0: IC6.141 (PE0), IC7.15 (LDQM)
/MCU, SDRAM/FMC_NBL1: IC6.142 (PE1), IC7.39 (UDQM)
/MCU, SDRAM/FMC_SDCKE0: IC6.45 (PC5), IC7.37 (CKE)
/MCU, SDRAM/FMC_SDCLK: IC6.93 (PG8), IC7.38 (CLK)
/MCU, SDRAM/FMC_SDNCAS: IC6.132 (PG15), IC7.17 (~CAS)
/MCU, SDRAM/FMC_SDNE0: IC6.44 (PC4), IC7.19 (~CS)
/MCU, SDRAM/FMC_SDNRAS: IC6.49 (PF11), IC7.18 (~RAS)
/MCU, SDRAM/FMC_SDNWE: IC6.43 (PA7), IC7.16 (~WE)
/MCU, SDRAM/RCC_OSC_IN: C34.2, IC6.23 (PH0-OSC_IN), Y1.1
/MCU, SDRAM/RCC_OSC_OUT: C35.2, IC6.24 (PH1-OSC_OUT), Y1.3
/MCU, SDRAM/SWCLK: IC6.109 (PA14), X3.4 (SWCLK)
/MCU, SDRAM/SWDIO: IC6.105 (PA13), X3.2 (SWDIO)
AFE_EXT_CLK: IC6.100 (PA8); also elsewhere on the board
AFE_SPI_MISO: IC6.112 (PC11); also elsewhere on the board
AFE_SPI_MOSI: IC6.113 (PC12); also elsewhere on the board
AFE_SPI_SCK: IC6.111 (PC10); also elsewhere on the board
CS_A0: IC6.104 (PA12); also elsewhere on the board
CS_A1: IC6.103 (PA11); also elsewhere on the board
CS_A2: IC6.102 (PA10); also elsewhere on the board
DIB_BOOT0: IC6.138 (BOOT0), R9.2; also elsewhere on the board
DIB_CSA: IC6.134 (PB4); also elsewhere on the board
DIB_MISO: IC6.75 (PB14); also elsewhere on the board
DIB_MOSI: IC6.27 (PC1); also elsewhere on the board
DIB_SCK: IC6.97 (PC7); also elsewhere on the board
DIB_SYNC: IC6.139 (PB8); also elsewhere on the board
GND: C16.2, C17.2, C18.1, C19.2, C20.2, C21.2, C22.2, C23.2, C24.2, C25.1, C27.1, C28.2, C29.2, C30.2, C31.2, C32.2, C33.2, C34.1, C35.1, C36.2, C37.2, C38.2, C39.2, C40.2, C41.2, C42.2, IC6.16 (VSS.16), IC6.31 (VSSA), IC6.38 (VSS.38), IC6.51 (VSS.51), IC6.61 (VSS.61), IC6.83 (VSS.83), IC6.94 (VSS.94), IC6.107 (VSS.107), IC6.120 (VSS.120), IC6.130 (VSS), IC7.6 (GNDQ-6), IC7.12 (GNDQ-12), IC7.28 (GND-28), IC7.41 (GND-41), IC7.46 (GNDQ-46), IC7.52 (GNDQ-52), IC7.54 (GND-54), LED1.C, R8.1, R9.1, X3.5 (GND); also elsewhere on the board
I2C_SCL: IC6.136 (PB6); also elsewhere on the board
I2C_SDA: IC6.137 (PB7); also elsewhere on the board
IO_SPI_MISO: IC6.4 (PE5); also elsewhere on the board
IO_SPI_MOSI: IC6.5 (PE6); also elsewhere on the board
IO_SPI_SCK: IC6.1 (PE2); also elsewhere on the board
unnamed: C26.2, R8.2
unnamed: IC6.7 (PC13), R70.2
unnamed: C18.2, IC6.6 (VBAT), JP1.2
unnamed: C27.2, IC6.71 (VCAP.71)
unnamed: C25.2, IC6.106 (VCAP.106)
unnamed: C16.1, C17.1, FB1.1, IC6.33 (VDDA), R7.1
unnamed: IC6.32 (VREF+), R7.2
unnamed: LED1.A, R70.1
PWM1: IC6.81 (PD12); also elsewhere on the board
PWM2: IC6.82 (PD13); also elsewhere on the board
USB_CLK: IC6.99 (PC9); also elsewhere on the board
USB_OTG_HS_ULPI_CK: IC6.41 (PA5); also elsewhere on the board
USB_OTG_HS_ULPI_D0: IC6.37 (PA3); also elsewhere on the board
USB_OTG_HS_ULPI_D1: IC6.46 (PB0); also elsewhere on the board
USB_OTG_HS_ULPI_D2: IC6.47 (PB1); also elsewhere on the board
USB_OTG_HS_ULPI_D3: IC6.69 (PB10); also elsewhere on the board
USB_OTG_HS_ULPI_D4: IC6.48 (PB2-BOOT1); also elsewhere on the board
USB_OTG_HS_ULPI_D5: IC6.73 (PB12); also elsewhere on the board
USB_OTG_HS_ULPI_D6: IC6.74 (PB13); also elsewhere on the board
USB_OTG_HS_ULPI_D7: IC6.135 (PB5); also elsewhere on the board
USB_OTG_HS_ULPI_DIR: IC6.28 (PC2); also elsewhere on the board
USB_OTG_HS_ULPI_NXT: IC6.29 (PC3); also elsewhere on the board
USB_OTG_HS_ULPI_STP: IC6.26 (PC0); also elsewhere on the board
USB_RESET: IC6.2 (PE3); also elsewhere on the board
~AFE_DRDY: IC6.101 (PA9); also elsewhere on the board
~DIB_FAULT: IC6.126 (PG11); also elsewhere on the board
~DIB_IRQ: IC6.22 (PF10); also elsewhere on the board
~DIB_RESET: D1.A, IC6.25 (NRST), R10.1, X3.3 (~RESET); also elsewhere on the board
~DIB_SHUTDOWN: D1.C; also elsewhere on the board
~IOEXP1_INT: IC6.116 (PD2); also elsewhere on the board
~IOEXP2_INT: IC6.117 (PD3); also elsewhere on the board
~IO_RESET: IC6.127 (PG12); also elsewhere on the board

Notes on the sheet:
3 nRST
SWO 6
32-bit MCU
SWCLK 4
SWDIO 2
1 N.C.
5 GND
PCB pads for WR-WST REDFIT IDC
Consumption: +3.3 V, up to 110 mA
SDRAM (64kbit, 4MBx16)
IMPORTANT: For PCB layout consult ST AN4661 section 8.4.2

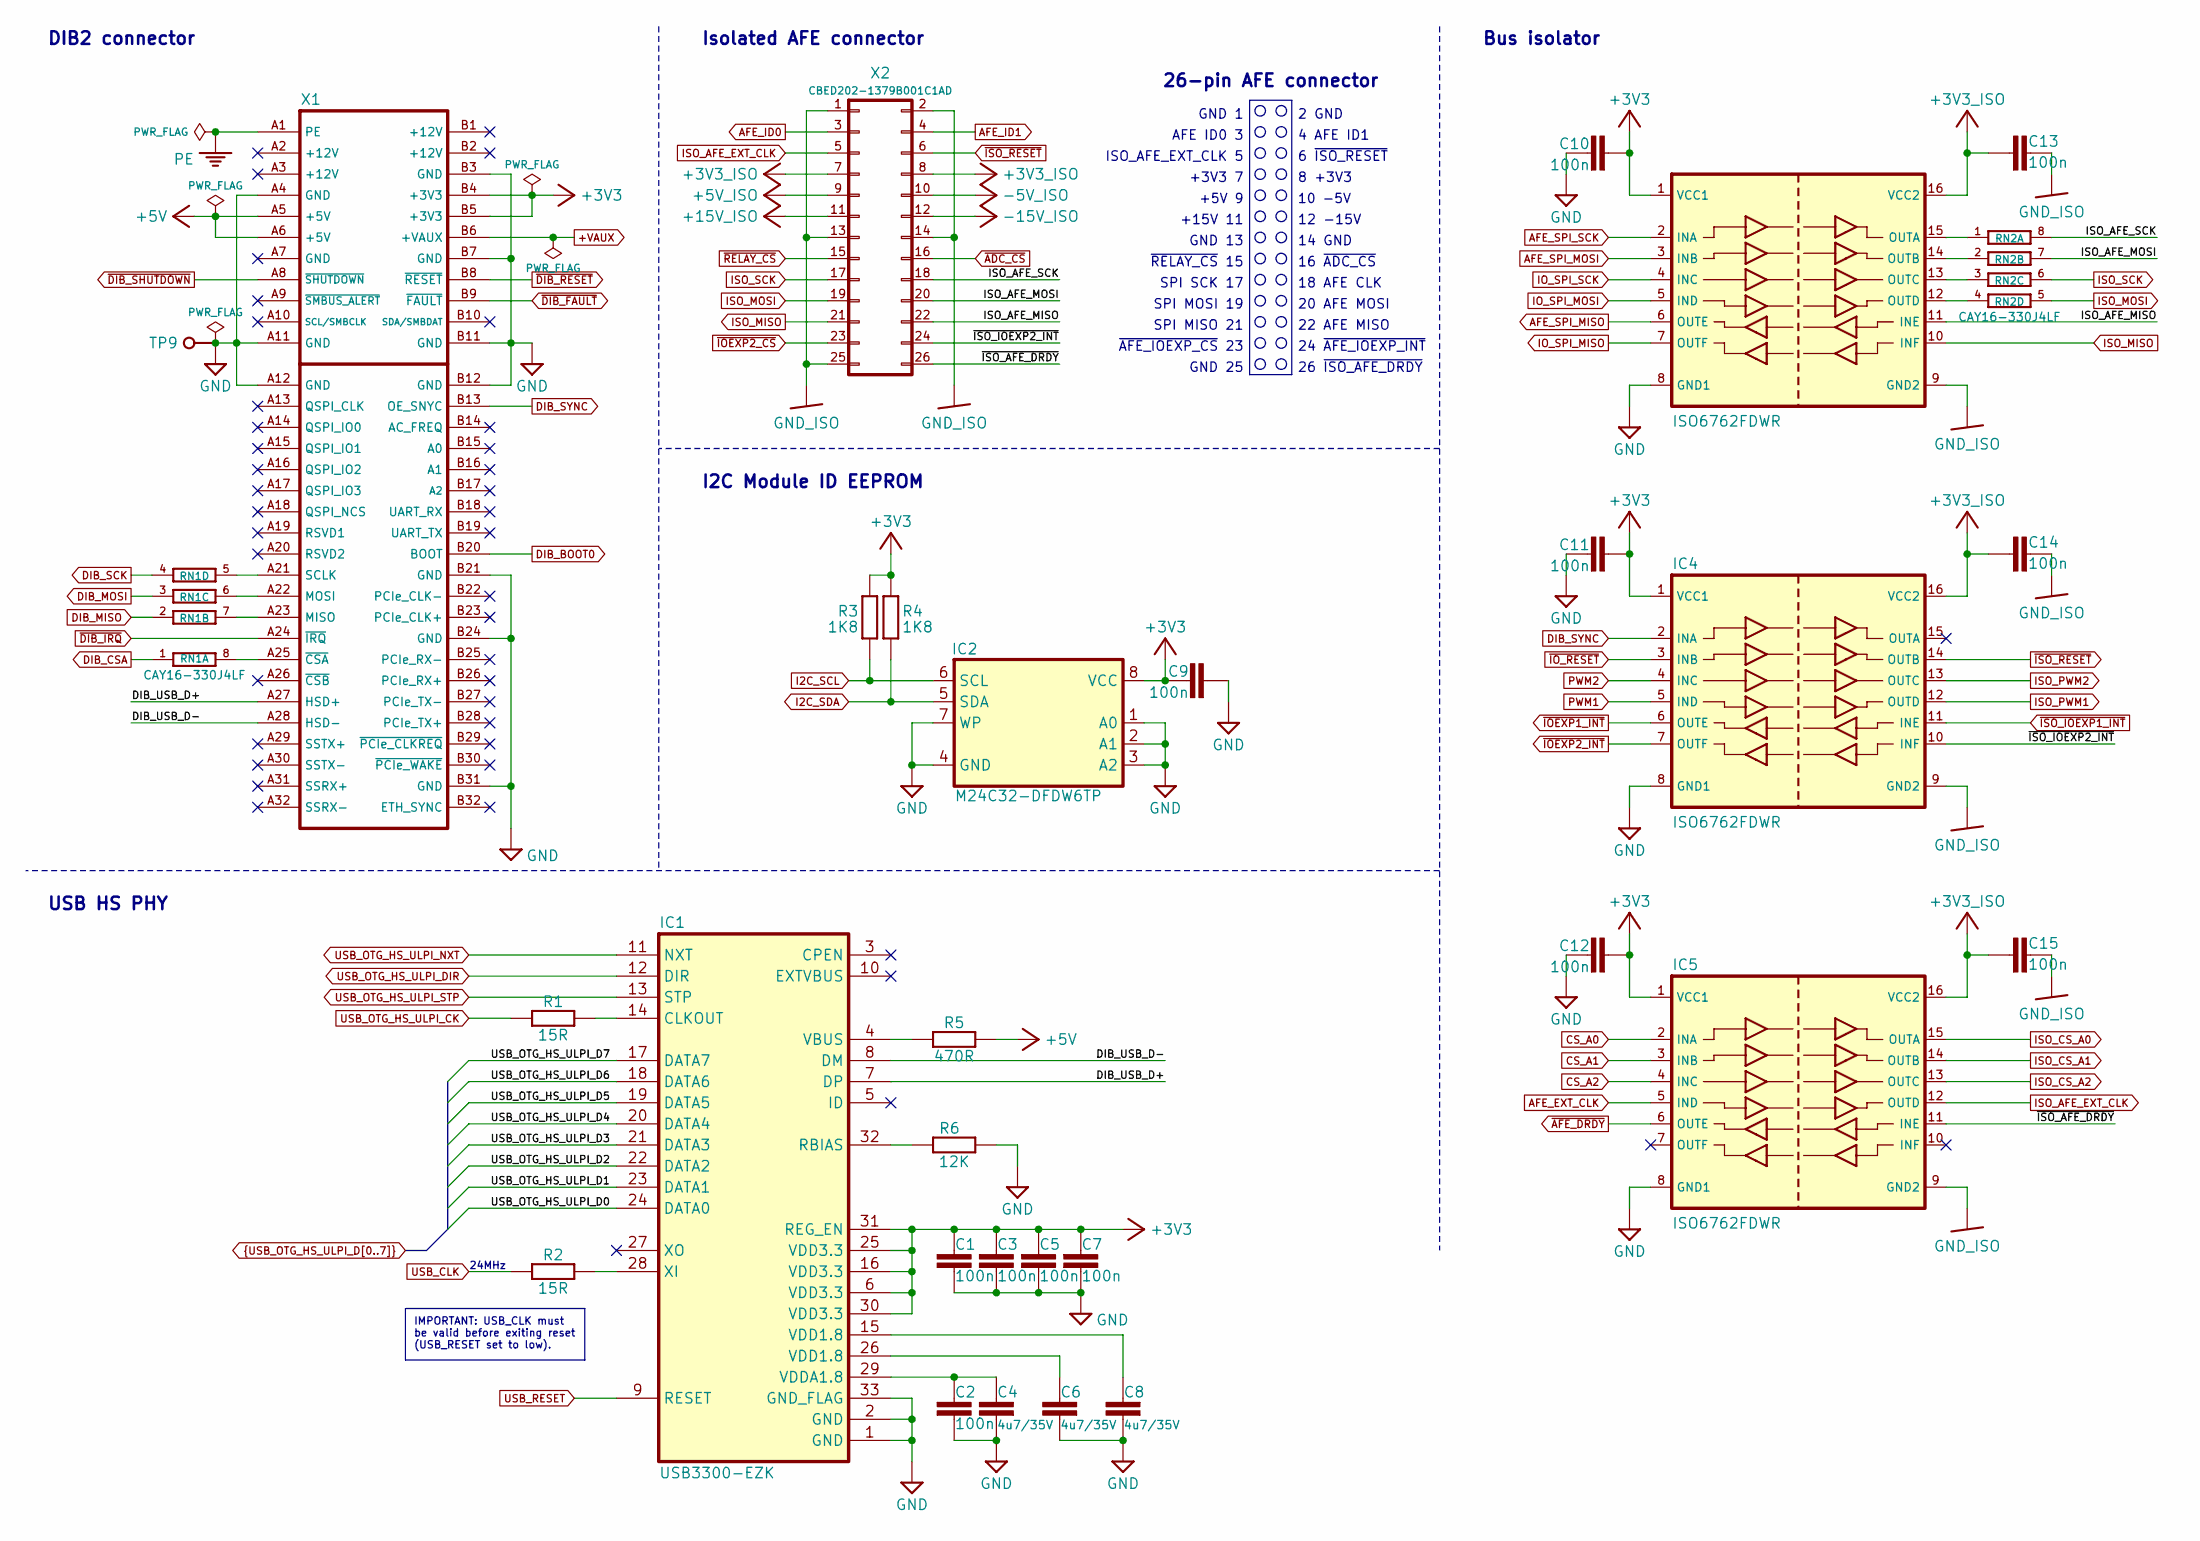
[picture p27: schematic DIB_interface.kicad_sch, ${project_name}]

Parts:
C1, C2, C3, C5, C7, C9, C10, C11, C12, C13, C14, C15: 100n; C_0603_1608Metric; DigiKey 490-4774-1-ND
C4, C6, C8: 4u7/35V; C_0603_1608Metric; DigiKey 1276-6794-1-ND
IC1: USB3300-EZK; QFN32_5X5MC_MCH-L; DigiKey 638-1034-ND
IC2: M24C32-DFDW6TP; TSSOP-8; DigiKey 497-16067-1-ND
IC3, IC4, IC5: ISO6762FDWR; DW16; DigiKey 296-ISO6762FDWRCT-ND
R1, R2: 15R; R_0603_1608Metric; DigiKey 13-AC0603FR-0715RLCT-ND
R3, R4: 1K8; R_0603_1608Metric; DigiKey 13-RC0603FR-131K8LCT-ND
R5: 470R; R_0603_1608Metric; DigiKey 13-AC0603FR-7W470RLCT-ND
R6: 12K; R_0603_1608Metric; DigiKey 13-RC0603FR-1312KLCT-ND
RN1, RN2: CAY16-330J4LF; CAY16; DigiKey CAY16-330J4LFCT-ND
TP9: Test; TEST-5
X1: DIB 2.0 edge card connector
X2: CBED202-1379B001C1AD; DigiKey 4217-CBED202-1379B001C1ADCT-ND

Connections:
+3V3: C1.1, C3.1, C5.1, C7.1, C9.2, C10.1, C11.1, C12.1, IC1.6 (VDD3.3), IC1.16 (VDD3.3), IC1.25 (VDD3.3), IC1.30 (VDD3.3), IC1.31 (REG_EN), IC2.8 (VCC), IC3.1 (VCC1), IC4.1 (VCC1), IC5.1 (VCC1), R3.1, R4.1, X1.B4 (+3V3), X1.B5 (+3V3); also elsewhere on the board
+3V3_ISO: C13.2, C14.2, C15.2, IC3.16 (VCC2), IC4.16 (VCC2), IC5.16 (VCC2), X2.7, X2.8; also elsewhere on the board
+5V: R5.1, X1.A5 (+5V), X1.A6 (+5V); also elsewhere on the board
+5V_ISO: X2.9; also elsewhere on the board
+15V_ISO: X2.11; also elsewhere on the board
+VAUX: X1.B6 (+VAUX); also elsewhere on the board
-5V_ISO: X2.10; also elsewhere on the board
-15V_ISO: X2.12; also elsewhere on the board
/DIB2 interface, USB PHY/DIB_USB_D+: IC1.7 (DP), X1.A27 (HSD+)
/DIB2 interface, USB PHY/DIB_USB_D-: IC1.8 (DM), X1.A28 (HSD-)
/DIB2 interface, USB PHY/ISO_AFE_MISO: IC3.11 (INE), X2.22
/DIB2 interface, USB PHY/ISO_AFE_MOSI: RN2.7 (2), X2.20
/DIB2 interface, USB PHY/ISO_AFE_SCK: RN2.8 (2), X2.18
/DIB2 interface, USB PHY/~ISO_AFE_DRDY: IC5.11 (INE), X2.26
/DIB2 interface, USB PHY/~ISO_IOEXP2_INT: IC4.10 (INF), X2.24
AFE_EXT_CLK: IC5.5 (IND); also elsewhere on the board
AFE_ID0: X2.3; also elsewhere on the board
AFE_ID1: X2.4; also elsewhere on the board
AFE_SPI_MISO: IC3.6 (OUTE); also elsewhere on the board
AFE_SPI_MOSI: IC3.3 (INB); also elsewhere on the board
AFE_SPI_SCK: IC3.2 (INA); also elsewhere on the board
CS_A0: IC5.2 (INA); also elsewhere on the board
CS_A1: IC5.3 (INB); also elsewhere on the board
CS_A2: IC5.4 (INC); also elsewhere on the board
DIB_BOOT0: X1.B20 (BOOT); also elsewhere on the board
DIB_CSA: RN1.1; also elsewhere on the board
DIB_MISO: RN1.2 (1); also elsewhere on the board
DIB_MOSI: RN1.3 (1); also elsewhere on the board
DIB_SCK: RN1.4 (1); also elsewhere on the board
DIB_SYNC: IC4.2 (INA), X1.B13 (OE_SNYC); also elsewhere on the board
GND: C1.2, C2.2, C3.2, C4.2, C5.2, C6.2, C7.2, C8.2, C9.1, C10.2, C11.2, C12.2, IC1.1 (GND), IC1.2 (GND), IC1.33 (GND_FLAG), IC2.1 (A0), IC2.2 (A1), IC2.3 (A2), IC2.4 (GND), IC2.7 (WP), IC3.8 (GND1), IC4.8 (GND1), IC5.8 (GND1), R6.1, TP9.1 (P$1_1), X1.A4 (GND), X1.A11 (GND), X1.A12 (GND), X1.B3 (GND), X1.B7 (GND), X1.B11 (GND), X1.B12 (GND), X1.B21 (GND), X1.B24 (GND), X1.B31 (GND); also elsewhere on the board
GND_ISO: C13.1, C14.1, C15.1, IC3.9 (GND2), IC4.9 (GND2), IC5.9 (GND2), X2.1, X2.2, X2.13, X2.14, X2.25; also elsewhere on the board
I2C_SCL: IC2.6 (SCL), R3.2; also elsewhere on the board
I2C_SDA: IC2.5 (SDA), R4.2; also elsewhere on the board
IO_SPI_MISO: IC3.7 (OUTF); also elsewhere on the board
IO_SPI_MOSI: IC3.5 (IND); also elsewhere on the board
IO_SPI_SCK: IC3.4 (INC); also elsewhere on the board
ISO_AFE_EXT_CLK: IC5.12 (OUTD), X2.5
ISO_CS_A0: IC5.15 (OUTA); also elsewhere on the board
ISO_CS_A1: IC5.14 (OUTB); also elsewhere on the board
ISO_CS_A2: IC5.13 (OUTC); also elsewhere on the board
ISO_MISO: IC3.10 (INF), X2.21; also elsewhere on the board
ISO_MOSI: RN2.5 (2), X2.19; also elsewhere on the board
ISO_PWM1: IC4.12 (OUTD); also elsewhere on the board
ISO_PWM2: IC4.13 (OUTC); also elsewhere on the board
ISO_SCK: RN2.6 (2), X2.17; also elsewhere on the board
unnamed: C6.1, IC1.26 (VDD1.8)
unnamed: C8.1, IC1.15 (VDD1.8)
unnamed: IC1.14 (CLKOUT), R1.1
unnamed: IC1.32 (RBIAS), R6.2
unnamed: IC1.4 (VBUS), R5.2
unnamed: C2.1, C4.1, IC1.29 (VDDA1.8)
unnamed: IC1.28 (XI), R2.1
unnamed: IC3.15 (OUTA), RN2.1
unnamed: IC3.14 (OUTB), RN2.2 (1)
unnamed: IC3.13 (OUTC), RN2.3 (1)
unnamed: IC3.12 (OUTD), RN2.4 (1)
unnamed: RN1.8 (2), X1.A25 (~CSA)
unnamed: RN1.7 (2), X1.A23 (MISO)
unnamed: RN1.6 (2), X1.A22 (MOSI)
unnamed: RN1.5 (2), X1.A21 (SCLK)
PE: X1.A1 (PE); also elsewhere on the board
PWM1: IC4.5 (IND); also elsewhere on the board
PWM2: IC4.4 (INC); also elsewhere on the board
USB_CLK: R2.2; also elsewhere on the board
USB_OTG_HS_ULPI_CK: R1.2; also elsewhere on the board
USB_OTG_HS_ULPI_D0: IC1.24 (DATA0); also elsewhere on the board
USB_OTG_HS_ULPI_D1: IC1.23 (DATA1); also elsewhere on the board
USB_OTG_HS_ULPI_D2: IC1.22 (DATA2); also elsewhere on the board
USB_OTG_HS_ULPI_D3: IC1.21 (DATA3); also elsewhere on the board
USB_OTG_HS_ULPI_D4: IC1.20 (DATA4); also elsewhere on the board
USB_OTG_HS_ULPI_D5: IC1.19 (DATA5); also elsewhere on the board
USB_OTG_HS_ULPI_D6: IC1.18 (DATA6); also elsewhere on the board
USB_OTG_HS_ULPI_D7: IC1.17 (DATA7); also elsewhere on the board
USB_OTG_HS_ULPI_DIR: IC1.12 (DIR); also elsewhere on the board
USB_OTG_HS_ULPI_NXT: IC1.11 (NXT); also elsewhere on the board
USB_OTG_HS_ULPI_STP: IC1.13 (STP); also elsewhere on the board
USB_RESET: IC1.9 (RESET); also elsewhere on the board
~ADC_CS: X2.16; also elsewhere on the board
~AFE_DRDY: IC5.6 (OUTE); also elsewhere on the board
~DIB_FAULT: X1.B9 (~FAULT); also elsewhere on the board
~DIB_IRQ: X1.A24 (~IRQ); also elsewhere on the board
~DIB_RESET: X1.B8 (~RESET); also elsewhere on the board
~DIB_SHUTDOWN: X1.A8 (~SHUTDOWN); also elsewhere on the board
~IOEXP1_INT: IC4.6 (OUTE); also elsewhere on the board
~IOEXP2_CS: X2.23; also elsewhere on the board
~IOEXP2_INT: IC4.7 (OUTF); also elsewhere on the board
~IO_RESET: IC4.3 (INB); also elsewhere on the board
~ISO_IOEXP1_INT: IC4.11 (INE); also elsewhere on the board
~ISO_RESET: IC4.14 (OUTB), X2.6; also elsewhere on the board
~RELAY_CS: X2.15; also elsewhere on the board

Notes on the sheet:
~{RELAY_CS} 15
6 ~{ISO_RESET}
2 GND
SPI SCK 17
18 AFE CLK
22 AFE MISO
4 AFE ID1
SPI MOSI 19
+15V 11
10 -5V
20 AFE MOSI
24 ~{AFE_IOEXP_INT}
GND 25
USB HS PHY
GND 1
AFE ID0 3
26-pin AFE connector
Isolated AFE connector
~{AFE_IOEXP_CS} 23
+5V 9
DIB2 connector
24MHz
ISO_AFE_EXT_CLK 5
12 -15V
I2C Module ID EEPROM
GND 13
+3V3 7
SPI MISO 21
14 GND
8 +3V3
26 ~{ISO_AFE_DRDY}
16 ~{ADC_CS}
Bus isolator
IMPORTANT: USB_CLK must be valid before exiting reset (USB_RESET set to low).

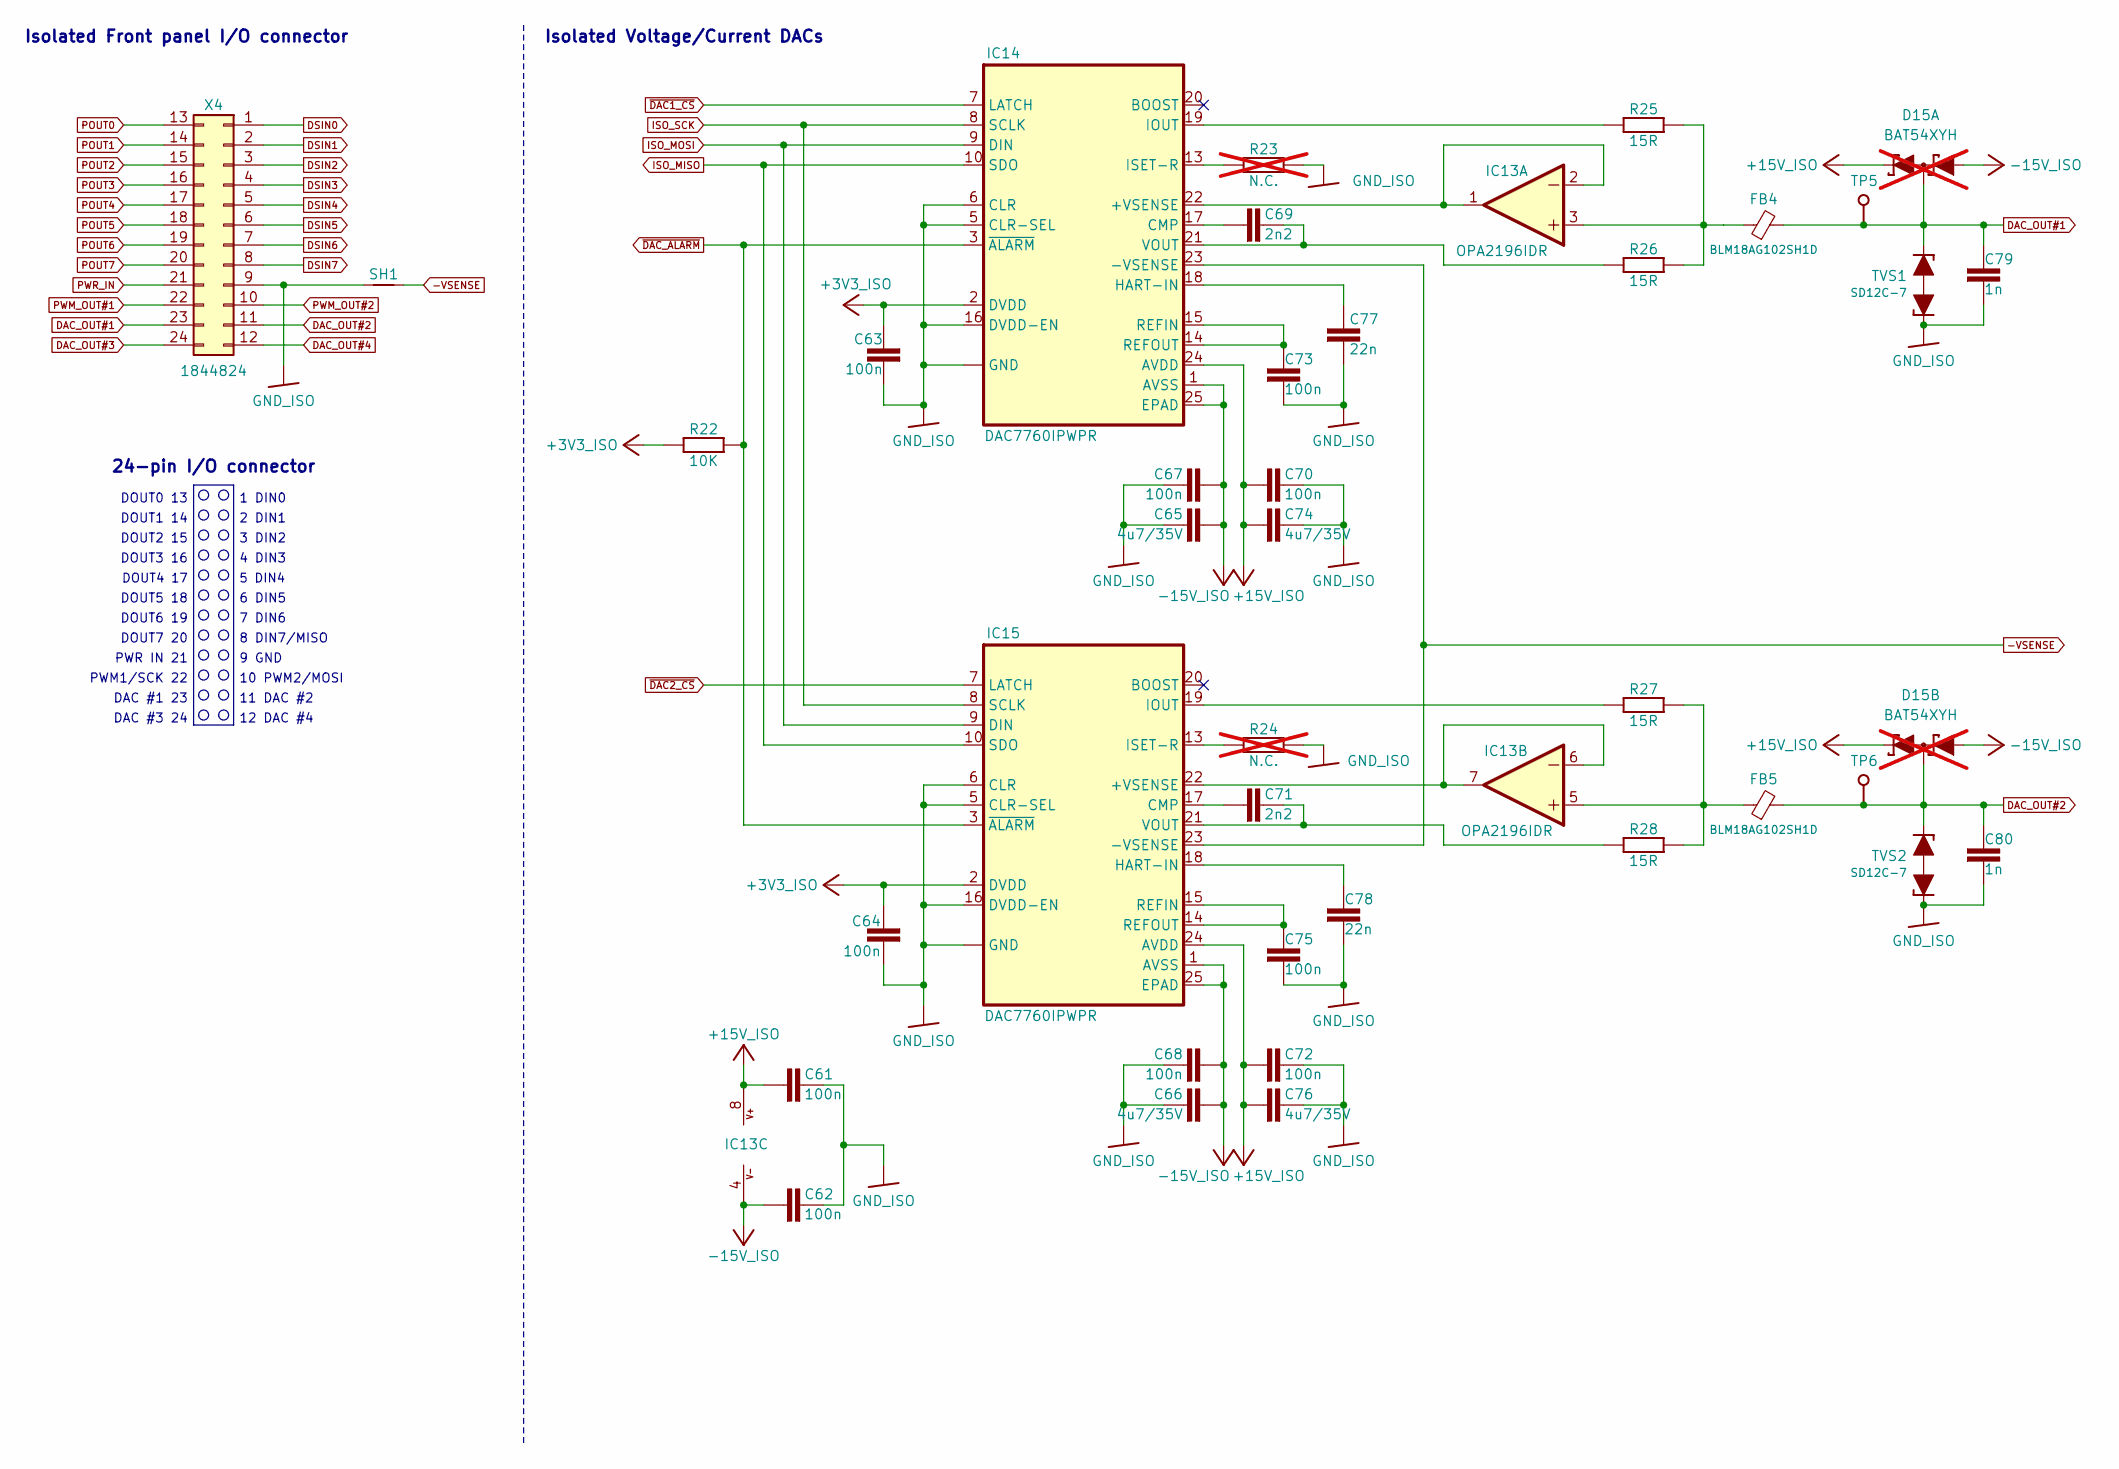
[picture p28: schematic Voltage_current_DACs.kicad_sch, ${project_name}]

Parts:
C61, C62, C63, C64, C67, C68, C70, C72, C73, C75: 100n; C_0603_1608Metric; DigiKey 490-4774-1-ND
C65, C66, C74, C76: 4u7/35V; C_0603_1608Metric; DigiKey 1276-6794-1-ND
C69, C71: 2n2; C_0603_1608Metric; DigiKey 490-4931-1-ND
C77, C78: 22n; C_0603_1608Metric; DigiKey 490-4933-1-ND
C79, C80: 1n; C_0603_1608Metric; DigiKey 1276-1018-2-ND
D15: BAT54XYH; SOP65P210X110-6N; DigiKey 1727-2723-1-ND; not fitted
FB4, FB5: BLM18AG102SH1D; BEAD0603; DigiKey 490-7809-1-ND
IC13: OPA2196IDR; SOIC127P600X173-8N; DigiKey 296-48159-1-ND
IC14, IC15: DAC7760IPWPR; PWP24; DigiKey 296-37188-1-ND
R22: 10K; R_0603_1608Metric; DigiKey 1712-CRGH0603F10KCT-ND
R23, R24: N.C.; R_0603_1608Metric; not fitted
R25, R26, R27, R28: 15R; R_0603_1608Metric; DigiKey 13-AC0603FR-0715RLCT-ND
SH1: SHORTNOHOLE; NetTie-2_SMD_Pad0.5mm
TP5, TP6: Test; Testhole 24_50mils
TVS1, TVS2: SD12C-7; SOD-323_PESD; DigiKey 31-SD12C-7CT-ND
X4: 1844824; DigiKey 1844824-ND

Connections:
+3V3_ISO: C63.1, C64.1, IC14.2 (DVDD), IC15.2 (DVDD), R22.1; also elsewhere on the board
+15V_ISO: C61.1, C70.1, C72.1, C74.2, C76.2, D15.2 (K2), D15.5 (K3), IC13.8 (V+), IC14.24 (AVDD), IC15.24 (AVDD); also elsewhere on the board
-15V_ISO: C62.1, C65.2, C66.2, C67.1, C68.1, D15.1 (A1), D15.4 (A4), IC13.4 (V-), IC14.1 (AVSS), IC14.25 (EPAD), IC15.1 (AVSS), IC15.25 (EPAD); also elsewhere on the board
-VSENSE: IC14.23 (-VSENSE), IC15.23 (-VSENSE), SH1.2
DAC_OUT#1: C79.1, D15.6 (K1A2), FB4.2, TP5.1 (P$1_1), TVS1.C2 (2), X4.23
DAC_OUT#2: C80.1, D15.3 (A3K4), FB5.2, TP6.1 (P$1_1), TVS2.C2 (2), X4.11
DAC_OUT#3: X4.24; also elsewhere on the board
DAC_OUT#4: X4.12; also elsewhere on the board
DSIN0: X4.1; also elsewhere on the board
DSIN1: X4.2; also elsewhere on the board
DSIN2: X4.3; also elsewhere on the board
DSIN3: X4.4; also elsewhere on the board
DSIN4: X4.5; also elsewhere on the board
DSIN5: X4.6; also elsewhere on the board
DSIN6: X4.7; also elsewhere on the board
DSIN7: X4.8; also elsewhere on the board
GND_ISO: C61.2, C62.2, C63.2, C64.2, C65.1, C66.1, C67.2, C68.2, C70.2, C72.2, C73.2, C74.1, C75.2, C76.1, C77.1, C78.1, C79.2, C80.2, IC14.4 (GND), IC14.5 (CLR-SEL), IC14.6 (CLR), IC14.11 (GND), IC14.12 (GND), IC14.16 (DVDD-EN), IC15.4 (GND), IC15.5 (CLR-SEL), IC15.6 (CLR), IC15.11 (GND), IC15.12 (GND), IC15.16 (DVDD-EN), R23.1, R24.2, SH1.1, TVS1.C1 (1), TVS2.C1 (1), X4.9; also elsewhere on the board
ISO_MISO: IC14.10 (SDO), IC15.10 (SDO); also elsewhere on the board
ISO_MOSI: IC14.9 (DIN), IC15.9 (DIN); also elsewhere on the board
ISO_SCK: IC14.8 (SCLK), IC15.8 (SCLK); also elsewhere on the board
unnamed: FB4.1, IC13.3 (+IN), R25.1, R26.1
unnamed: IC13.1 (OUT), IC13.2 (-IN), IC14.22 (+VSENSE)
unnamed: FB5.1, IC13.5 (+IN), R27.1, R28.1
unnamed: IC13.6 (-IN), IC13.7 (OUT), IC15.22 (+VSENSE)
unnamed: C69.2, IC14.17 (CMP)
unnamed: C77.2, IC14.18 (HART-IN)
unnamed: IC14.19 (IOUT), R25.2
unnamed: IC14.13 (ISET-R), R23.2
unnamed: C73.1, IC14.14 (REFOUT), IC14.15 (REFIN)
unnamed: C69.1, IC14.21 (VOUT), R26.2
unnamed: C71.2, IC15.17 (CMP)
unnamed: C78.2, IC15.18 (HART-IN)
unnamed: IC15.19 (IOUT), R27.2
unnamed: IC15.13 (ISET-R), R24.1
unnamed: C75.1, IC15.14 (REFOUT), IC15.15 (REFIN)
unnamed: C71.1, IC15.21 (VOUT), R28.2
POUT0: X4.13; also elsewhere on the board
POUT1: X4.14; also elsewhere on the board
POUT2: X4.15; also elsewhere on the board
POUT3: X4.16; also elsewhere on the board
POUT4: X4.17; also elsewhere on the board
POUT5: X4.18; also elsewhere on the board
POUT6: X4.19; also elsewhere on the board
POUT7: X4.20; also elsewhere on the board
PWM_OUT#1: X4.22; also elsewhere on the board
PWM_OUT#2: X4.10; also elsewhere on the board
PWR_IN: X4.21; also elsewhere on the board
~DAC1_CS: IC14.7 (LATCH); also elsewhere on the board
~DAC2_CS: IC15.7 (LATCH); also elsewhere on the board
~DAC_ALARM: IC14.3 (~ALARM), IC15.3 (~ALARM), R22.2; also elsewhere on the board

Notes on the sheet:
Isolated Voltage/Current DACs
1 DIN0
9 GND
DAC #1 23
DAC #3 24
DOUT2 15
6 DIN5
24-pin I/O connector
PWR IN 21
12 DAC #4
DOUT3 16
DOUT7 20
3 DIN2
4 DIN3
8 DIN7/MISO
DOUT5 18
11 DAC #2
2 DIN1
DOUT1 14
5 DIN4
Isolated Front panel I/O connector
7 DIN6
PWM1/SCK 22
DOUT6 19
DOUT4 17
DOUT0 13
10 PWM2/MOSI

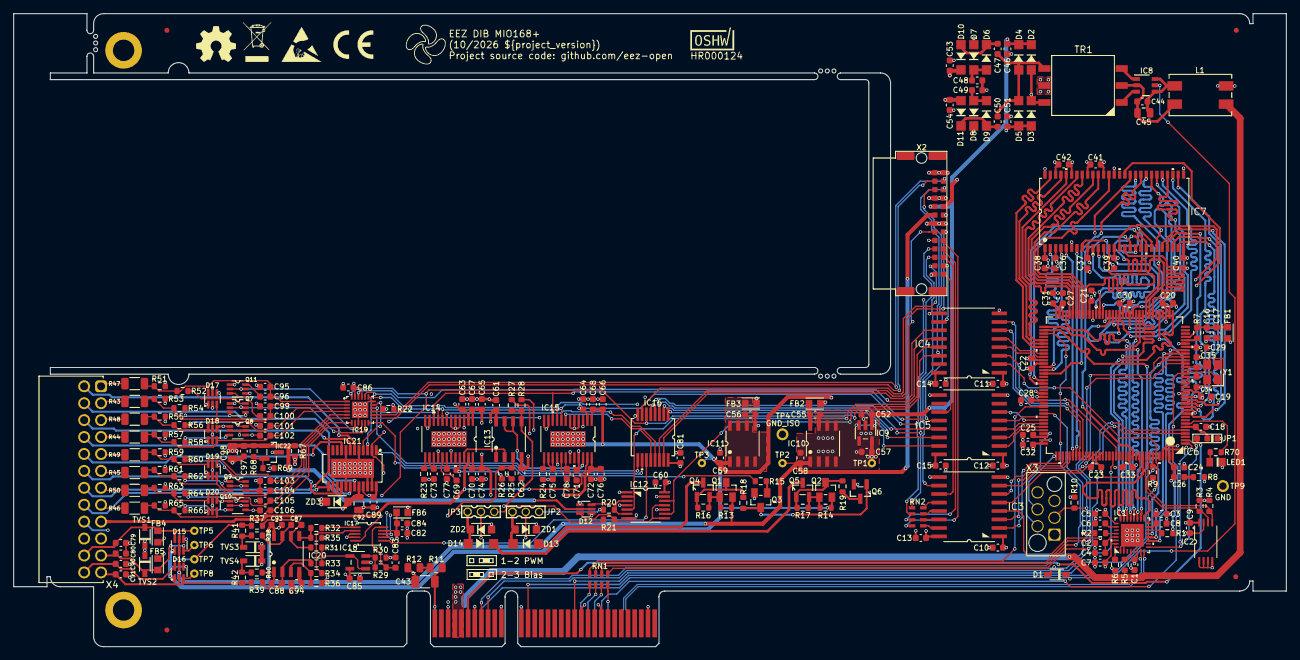
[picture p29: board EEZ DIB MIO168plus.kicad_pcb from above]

Board: 4 copper layers, 191.0 x 95.0 mm, 277 parts (0 on the bottom side), 255 nets.

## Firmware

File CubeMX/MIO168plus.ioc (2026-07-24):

#MicroXplorer Configuration settings - do not modify
CAD.formats=
CAD.pinconfig=
CAD.provider=
File.Version=6
GPIO.groupedBy=Group By Peripherals
KeepUserPlacement=false
Mcu.CPN=STM32F446ZET6
Mcu.Family=STM32F4
Mcu.IP0=FMC
Mcu.IP1=I2C1
Mcu.IP2=NVIC
Mcu.IP3=RCC
Mcu.IP4=SPI2
Mcu.IP5=SPI3
Mcu.IP6=SPI4
Mcu.IP7=SYS
Mcu.IP8=TIM4
Mcu.IP9=USB_OTG_HS
Mcu.IPNb=10
Mcu.Name=STM32F446Z(C-E)Tx
Mcu.Package=LQFP144
Mcu.Pin0=PE2
Mcu.Pin1=PE3
Mcu.Pin10=PF5
Mcu.Pin11=PF10
Mcu.Pin12=PH0-OSC_IN
Mcu.Pin13=PH1-OSC_OUT
Mcu.Pin14=PC0
Mcu.Pin15=PC1
Mcu.Pin16=PC2
Mcu.Pin17=PC3
Mcu.Pin18=PA3
Mcu.Pin19=PA4
Mcu.Pin2=PE4
Mcu.Pin20=PA5
Mcu.Pin21=PA7
Mcu.Pin22=PC4
Mcu.Pin23=PC5
Mcu.Pin24=PB0
Mcu.Pin25=PB1
Mcu.Pin26=PB2
Mcu.Pin27=PF11
Mcu.Pin28=PF12
Mcu.Pin29=PF13
Mcu.Pin3=PE5
Mcu.Pin30=PF14
Mcu.Pin31=PF15
Mcu.Pin32=PG0
Mcu.Pin33=PG1
Mcu.Pin34=PE7
Mcu.Pin35=PE8
Mcu.Pin36=PE9
Mcu.Pin37=PE10
Mcu.Pin38=PE11
Mcu.Pin39=PE12
Mcu.Pin4=PE6
Mcu.Pin40=PE13
Mcu.Pin41=PE14
Mcu.Pin42=PE15
Mcu.Pin43=PB10
Mcu.Pin44=PB12
Mcu.Pin45=PB13
Mcu.Pin46=PB14
Mcu.Pin47=PD8
Mcu.Pin48=PD9
Mcu.Pin49=PD10
Mcu.Pin5=PF0
Mcu.Pin50=PD12
Mcu.Pin51=PD13
Mcu.Pin52=PD14
Mcu.Pin53=PD15
Mcu.Pin54=PG2
Mcu.Pin55=PG4
Mcu.Pin56=PG5
Mcu.Pin57=PG8
Mcu.Pin58=PC7
Mcu.Pin59=PC9
Mcu.Pin6=PF1
Mcu.Pin60=PA8
Mcu.Pin61=PA9
Mcu.Pin62=PA10
Mcu.Pin63=PA11
Mcu.Pin64=PA12
Mcu.Pin65=PA13
Mcu.Pin66=PA14
Mcu.Pin67=PC10
Mcu.Pin68=PC11
Mcu.Pin69=PC12
Mcu.Pin7=PF2
Mcu.Pin70=PD0
Mcu.Pin71=PD1
Mcu.Pin72=PD2
Mcu.Pin73=PD3
Mcu.Pin74=PG11
Mcu.Pin75=PG12
Mcu.Pin76=PG15
Mcu.Pin77=PB4
Mcu.Pin78=PB5
Mcu.Pin79=PB6
Mcu.Pin8=PF3
Mcu.Pin80=PB7
Mcu.Pin81=PB8
Mcu.Pin82=PE0
Mcu.Pin83=PE1
Mcu.Pin84=VP_SYS_VS_Systick
Mcu.Pin9=PF4
Mcu.PinsNb=85
Mcu.ThirdPartyNb=0
Mcu.UserConstants=
Mcu.UserName=STM32F446ZETx
MxCube.Version=6.17.0
MxDb.Version=DB.6.0.170
NVIC.BusFault_IRQn=true\:0\:0\:false\:false\:true\:false\:false\:false
NVIC.DebugMonitor_IRQn=true\:0\:0\:false\:false\:true\:false\:false\:false
NVIC.ForceEnableDMAVector=true
NVIC.HardFault_IRQn=true\:0\:0\:false\:false\:true\:false\:false\:false
NVIC.MemoryManagement_IRQn=true\:0\:0\:false\:false\:true\:false\:false\:false
NVIC.NonMaskableInt_IRQn=true\:0\:0\:false\:false\:true\:false\:false\:false
NVIC.PendSV_IRQn=true\:0\:0\:false\:false\:true\:false\:false\:false
NVIC.PriorityGroup=NVIC_PRIORITYGROUP_4
NVIC.SVCall_IRQn=true\:0\:0\:false\:false\:true\:false\:false\:false
NVIC.SysTick_IRQn=true\:15\:0\:false\:false\:true\:false\:true\:false
NVIC.UsageFault_IRQn=true\:0\:0\:false\:false\:true\:false\:false\:false
PA10.GPIOParameters=GPIO_Label
PA10.GPIO_Label=CS_A2
PA10.Locked=true
PA10.Signal=GPIO_Output
PA11.GPIOParameters=GPIO_Label
PA11.GPIO_Label=CS_A1
PA11.Locked=true
PA11.Signal=GPIO_Output
PA12.GPIOParameters=GPIO_Label
PA12.GPIO_Label=CS_A0
PA12.Locked=true
PA12.Signal=GPIO_Output
PA13.Mode=Serial_Wire
PA13.Signal=SYS_JTMS-SWDIO
PA14.Mode=Serial_Wire
PA14.Signal=SYS_JTCK-SWCLK
PA3.Mode=Device_HS
PA3.Signal=USB_OTG_HS_ULPI_D0
PA4.Mode=NSS_Signal_Hard_Output
PA4.Signal=SPI3_NSS
PA5.Mode=Device_HS
PA5.Signal=USB_OTG_HS_ULPI_CK
PA7.Signal=FMC_SDNWE
PA8.GPIOParameters=GPIO_Label
PA8.GPIO_Label=AFE_EXT_CLK
PA8.Locked=true
PA8.Mode=Clock-out-1
PA8.Signal=RCC_MCO_1
PA9.GPIOParameters=GPIO_Label
PA9.GPIO_Label=AFE_DRDY
PA9.Locked=true
PA9.Signal=GPXTI9
PB0.Mode=Device_HS
PB0.Signal=USB_OTG_HS_ULPI_D1
PB1.Mode=Device_HS
PB1.Signal=USB_OTG_HS_ULPI_D2
PB10.Mode=Device_HS
PB10.Signal=USB_OTG_HS_ULPI_D3
PB12.Mode=Device_HS
PB12.Signal=USB_OTG_HS_ULPI_D5
PB13.Mode=Device_HS
PB13.Signal=USB_OTG_HS_ULPI_D6
PB14.GPIOParameters=GPIO_Label
PB14.GPIO_Label=DIB_MISO
PB14.Mode=Full_Duplex_Slave
PB14.Signal=SPI2_MISO
PB2.Mode=Device_HS
PB2.Signal=USB_OTG_HS_ULPI_D4
PB4.GPIOParameters=GPIO_Label
PB4.GPIO_Label=DIB_CSA
PB4.Mode=NSS_Signal_Hard_Input
PB4.Signal=SPI2_NSS
PB5.Mode=Device_HS
PB5.Signal=USB_OTG_HS_ULPI_D7
PB6.Mode=I2C
PB6.Signal=I2C1_SCL
PB7.Mode=I2C
PB7.Signal=I2C1_SDA
PB8.GPIOParameters=GPIO_Label
PB8.GPIO_Label=DIB_OE_SYNC
PB8.Locked=true
PB8.Signal=GPXTI8
PC0.Mode=Device_HS
PC0.Signal=USB_OTG_HS_ULPI_STP
PC1.GPIOParameters=GPIO_Label
PC1.GPIO_Label=DIB_MOSI
PC1.Mode=Full_Duplex_Slave
PC1.Signal=SPI2_MOSI
PC10.Mode=Full_Duplex_Master
PC10.Signal=SPI3_SCK
PC11.Mode=Full_Duplex_Master
PC11.Signal=SPI3_MISO
PC12.Mode=Full_Duplex_Master
PC12.Signal=SPI3_MOSI
PC2.Mode=Device_HS
PC2.Signal=USB_OTG_HS_ULPI_DIR
PC3.Mode=Device_HS
PC3.Signal=USB_OTG_HS_ULPI_NXT
PC4.Mode=SdramChipSelect1_1
PC4.Signal=FMC_SDNE0
PC5.Mode=SdramChipSelect1_1
PC5.Signal=FMC_SDCKE0
PC7.GPIOParameters=GPIO_Label
PC7.GPIO_Label=DIB_SCK
PC7.Mode=Full_Duplex_Slave
PC7.Signal=SPI2_SCK
PC9.GPIOParameters=GPIO_Label
PC9.GPIO_Label=USB_CLK
PC9.Locked=true
PC9.Mode=Clock-out-2
PC9.Signal=RCC_MCO_2
PCC.Checker=false
PCC.Display=Plot\: All Steps
PCC.Line=STM32F446
PCC.MCU=STM32F446Z(C-E)Tx
PCC.PartNumber=STM32F446ZETx
PCC.Series=STM32F4
PCC.Temperature=25
PCC.Vdd=3.3
PD0.Signal=FMC_D2_DA2
PD1.Signal=FMC_D3_DA3
PD10.Signal=FMC_D15_DA15
PD12.GPIOParameters=GPIO_Label
PD12.GPIO_Label=PWM1
PD12.Signal=S_TIM4_CH1
PD13.GPIOParameters=GPIO_Label
PD13.GPIO_Label=PWM2
PD13.Signal=S_TIM4_CH2
PD14.Signal=FMC_D0_DA0
PD15.Signal=FMC_D1_DA1
PD2.GPIOParameters=GPIO_Label
PD2.GPIO_Label=IOEXP1_INT
PD2.Locked=true
PD2.Signal=GPXTI2
PD3.GPIOParameters=GPIO_Label
PD3.GPIO_Label=IOEXP2_INT
PD3.Locked=true
PD3.Signal=GPXTI3
PD8.Signal=FMC_D13_DA13
PD9.Signal=FMC_D14_DA14
PE0.Signal=FMC_NBL0
PE1.Signal=FMC_NBL1
PE10.Signal=FMC_D7_DA7
PE11.Signal=FMC_D8_DA8
PE12.Signal=FMC_D9_DA9
PE13.Signal=FMC_D10_DA10
PE14.Signal=FMC_D11_DA11
PE15.Signal=FMC_D12_DA12
PE2.Mode=Full_Duplex_Master
PE2.Signal=SPI4_SCK
PE3.GPIOParameters=GPIO_Label
PE3.GPIO_Label=USB_RESET
PE3.Locked=true
PE3.Signal=GPIO_Output
PE4.Mode=NSS_Signal_Hard_Output
PE4.Signal=SPI4_NSS
PE5.Mode=Full_Duplex_Master
PE5.Signal=SPI4_MISO
PE6.Mode=Full_Duplex_Master
PE6.Signal=SPI4_MOSI
PE7.Signal=FMC_D4_DA4
PE8.Signal=FMC_D5_DA5
PE9.Signal=FMC_D6_DA6
PF0.Signal=FMC_A0
PF1.Signal=FMC_A1
PF10.GPIOParameters=GPIO_Label
PF10.GPIO_Label=DIB_IRQ
PF10.Locked=true
PF10.Signal=GPIO_Output
PF11.Signal=FMC_SDNRAS
PF12.Signal=FMC_A6
PF13.Signal=FMC_A7
PF14.Signal=FMC_A8
PF15.Signal=FMC_A9
PF2.Signal=FMC_A2
PF3.Signal=FMC_A3
PF4.Signal=FMC_A4
PF5.Signal=FMC_A5
PG0.Signal=FMC_A10
PG1.Signal=FMC_A11
PG11.GPIOParameters=GPIO_Label
PG11.GPIO_Label=DIB_FAULT
PG11.Locked=true
PG11.Signal=GPXTI11
PG12.GPIOParameters=GPIO_Label
PG12.GPIO_Label=IO_RESET
PG12.Locked=true
PG12.Signal=GPIO_Output
PG15.Signal=FMC_SDNCAS
PG2.Signal=FMC_A12
PG4.Signal=FMC_A14_BA0
PG5.Signal=FMC_A15_BA1
PG8.Signal=FMC_SDCLK
PH0-OSC_IN.Mode=HSE-External-Oscillator
PH0-OSC_IN.Signal=RCC_OSC_IN
PH1-OSC_OUT.Mode=HSE-External-Oscillator
PH1-OSC_OUT.Signal=RCC_OSC_OUT
PinOutPanel.RotationAngle=0
ProjectManager.AskForMigrate=true
ProjectManager.BackupPrevious=false
ProjectManager.CompilerLinker=GCC
ProjectManager.CompilerOptimize=6
ProjectManager.ComputerToolchain=false
ProjectManager.CoupleFile=false
ProjectManager.CustomerFirmwarePackage=
ProjectManager.DefaultFWLocation=true
ProjectManager.DeletePrevious=true
ProjectManager.DeviceId=STM32F446ZETx
ProjectManager.FirmwarePackage=STM32Cube FW_F4 V1.28.3
ProjectManager.FreePins=false
ProjectManager.FreePinsContext=
ProjectManager.HalAssertFull=false
ProjectManager.HeapSize=0x200
ProjectManager.KeepUserCode=true
ProjectManager.LastFirmware=true
ProjectManager.LibraryCopy=0
ProjectManager.MainLocation=Core/Src
ProjectManager.NoMain=false
ProjectManager.PreviousToolchain=
ProjectManager.ProjectBuild=false
ProjectManager.ProjectFileName=MIO168plus.ioc
ProjectManager.ProjectName=MIO168plus
ProjectManager.ProjectStructure=
ProjectManager.RegisterCallBack=
ProjectManager.StackSize=0x400
ProjectManager.TargetToolchain=EWARM V8.50
ProjectManager.ToolChainLocation=
ProjectManager.UAScriptAfterPath=
ProjectManager.UAScriptBeforePath=
ProjectManager.UnderRoot=false
ProjectManager.functionlistsort=1-SystemClock_Config-RCC-false-HAL-false,2-MX_GPIO_Init-GPIO-false-HAL-true,3-MX_FMC_Init-FMC-false-HAL-true,4-MX_I2C1_Init-I2C1-false-HAL-true,5-MX_SPI2_Init-SPI2-false-HAL-true,6-MX_SPI3_Init-SPI3-false-HAL-true,7-MX_SPI4_Init-SPI4-false-HAL-true,8-MX_USB_OTG_HS_PCD_Init-USB_OTG_HS-false-HAL-true,9-MX_TIM2_Init-TIM2-false-HAL-true
RCC.AHBFreq_Value=180000000
RCC.APB1CLKDivider=RCC_HCLK_DIV4
RCC.APB1Freq_Value=45000000
RCC.APB1TimFreq_Value=90000000
RCC.APB2CLKDivider=RCC_HCLK_DIV2
RCC.APB2Freq_Value=90000000
RCC.APB2TimFreq_Value=180000000
RCC.CECFreq_Value=32786.88524590164
RCC.CortexFreq_Value=180000000
RCC.FCLKCortexFreq_Value=180000000
RCC.FMPI2C1Freq_Value=45000000
RCC.FamilyName=M
RCC.HCLKFreq_Value=180000000
RCC.HSE_VALUE=16000000
RCC.I2S1Freq_Value=96000000
RCC.I2S2Freq_Value=96000000
RCC.IPParameters=AHBFreq_Value,APB1CLKDivider,APB1Freq_Value,APB1TimFreq_Value,APB2CLKDivider,APB2Freq_Value,APB2TimFreq_Value,CECFreq_Value,CortexFreq_Value,FCLKCortexFreq_Value,FMPI2C1Freq_Value,FamilyName,HCLKFreq_Value,HSE_VALUE,I2S1Freq_Value,I2S2Freq_Value,MCO1PinFreq_Value,MCO2PinFreq_Value,PLLCLKFreq_Value,PLLI2SM,PLLI2SPCLKFreq_Value,PLLI2SQCLKFreq_Value,PLLI2SR,PLLI2SRCLKFreq_Value,PLLI2SoutputFreq_Value,PLLM,PLLN,PLLQCLKFreq_Value,PLLRCLKFreq_Value,PLLSAIPCLKFreq_Value,PLLSAIQCLKFreq_Value,PLLSAIoutputFreq_Value,PLLSourceVirtual,PWRFreq_Value,RCC_MCO1Source,RCC_MCO2Source,RCC_MCODiv2,SAIAFreq_Value,SAIBFreq_Value,SDIOFreq_Value,SPDIFRXFreq_Value,SYSCLKFreq_VALUE,SYSCLKSource,USBFreq_Value,VCOI2SInputFreq_Value,VCOI2SOutputFreq_Value,VCOInputFreq_Value,VCOOutputFreq_Value,VCOSAIInputFreq_Value,VCOSAIOutputFreq_Value
RCC.MCO1PinFreq_Value=16000000
RCC.MCO2PinFreq_Value=24000000
RCC.PLLCLKFreq_Value=180000000
RCC.PLLI2SM=8
RCC.PLLI2SPCLKFreq_Value=192000000
RCC.PLLI2SQCLKFreq_Value=192000000
RCC.PLLI2SR=4
RCC.PLLI2SRCLKFreq_Value=96000000
RCC.PLLI2SoutputFreq_Value=192000000
RCC.PLLM=8
RCC.PLLN=180
RCC.PLLQCLKFreq_Value=180000000
RCC.PLLRCLKFreq_Value=180000000
RCC.PLLSAIPCLKFreq_Value=96000000
RCC.PLLSAIQCLKFreq_Value=96000000
RCC.PLLSAIoutputFreq_Value=96000000
RCC.PLLSourceVirtual=RCC_PLLSOURCE_HSE
RCC.PWRFreq_Value=180000000
RCC.RCC_MCO1Source=RCC_MCO1SOURCE_HSE
RCC.RCC_MCO2Source=RCC_MCO2SOURCE_PLLI2SCLK
RCC.RCC_MCODiv2=RCC_MCODIV_4
RCC.SAIAFreq_Value=96000000
RCC.SAIBFreq_Value=96000000
RCC.SDIOFreq_Value=180000000
RCC.SPDIFRXFreq_Value=180000000
RCC.SYSCLKFreq_VALUE=180000000
RCC.SYSCLKSource=RCC_SYSCLKSOURCE_PLLRCLK
RCC.USBFreq_Value=180000000
RCC.VCOI2SInputFreq_Value=2000000
RCC.VCOI2SOutputFreq_Value=384000000
RCC.VCOInputFreq_Value=2000000
RCC.VCOOutputFreq_Value=360000000
RCC.VCOSAIInputFreq_Value=1000000
RCC.VCOSAIOutputFreq_Value=192000000
SH.FMC_A0.0=FMC_A0,13b-sda1
SH.FMC_A0.ConfNb=1
SH.FMC_A1.0=FMC_A1,13b-sda1
SH.FMC_A1.ConfNb=1
SH.FMC_A10.0=FMC_A10,13b-sda1
SH.FMC_A10.ConfNb=1
SH.FMC_A11.0=FMC_A11,13b-sda1
SH.FMC_A11.ConfNb=1
SH.FMC_A12.0=FMC_A12,13b-sda1
SH.FMC_A12.ConfNb=1
SH.FMC_A14_BA0.0=FMC_BA0,FourSdramBanks1
SH.FMC_A14_BA0.ConfNb=1
SH.FMC_A15_BA1.0=FMC_BA1,FourSdramBanks1
SH.FMC_A15_BA1.ConfNb=1
SH.FMC_A2.0=FMC_A2,13b-sda1
SH.FMC_A2.ConfNb=1
SH.FMC_A3.0=FMC_A3,13b-sda1
SH.FMC_A3.ConfNb=1
SH.FMC_A4.0=FMC_A4,13b-sda1
SH.FMC_A4.ConfNb=1
SH.FMC_A5.0=FMC_A5,13b-sda1
SH.FMC_A5.ConfNb=1
SH.FMC_A6.0=FMC_A6,13b-sda1
SH.FMC_A6.ConfNb=1
SH.FMC_A7.0=FMC_A7,13b-sda1
SH.FMC_A7.ConfNb=1
SH.FMC_A8.0=FMC_A8,13b-sda1
SH.FMC_A8.ConfNb=1
SH.FMC_A9.0=FMC_A9,13b-sda1
SH.FMC_A9.ConfNb=1
SH.FMC_D0_DA0.0=FMC_D0,sd-16b-d1
SH.FMC_D0_DA0.ConfNb=1
SH.FMC_D10_DA10.0=FMC_D10,sd-16b-d1
SH.FMC_D10_DA10.ConfNb=1
SH.FMC_D11_DA11.0=FMC_D11,sd-16b-d1
SH.FMC_D11_DA11.ConfNb=1
SH.FMC_D12_DA12.0=FMC_D12,sd-16b-d1
SH.FMC_D12_DA12.ConfNb=1
SH.FMC_D13_DA13.0=FMC_D13,sd-16b-d1
SH.FMC_D13_DA13.ConfNb=1
SH.FMC_D14_DA14.0=FMC_D14,sd-16b-d1
SH.FMC_D14_DA14.ConfNb=1
SH.FMC_D15_DA15.0=FMC_D15,sd-16b-d1
SH.FMC_D15_DA15.ConfNb=1
SH.FMC_D1_DA1.0=FMC_D1,sd-16b-d1
SH.FMC_D1_DA1.ConfNb=1
SH.FMC_D2_DA2.0=FMC_D2,sd-16b-d1
SH.FMC_D2_DA2.ConfNb=1
SH.FMC_D3_DA3.0=FMC_D3,sd-16b-d1
SH.FMC_D3_DA3.ConfNb=1
SH.FMC_D4_DA4.0=FMC_D4,sd-16b-d1
SH.FMC_D4_DA4.ConfNb=1
SH.FMC_D5_DA5.0=FMC_D5,sd-16b-d1
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

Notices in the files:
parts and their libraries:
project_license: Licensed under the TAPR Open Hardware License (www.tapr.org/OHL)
